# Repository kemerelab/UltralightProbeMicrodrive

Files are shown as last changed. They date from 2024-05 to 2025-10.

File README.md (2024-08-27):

# UltralightProbeMicrodrive
Ultra-light microdrive design for implanted multichannel neural recording probes. 
Remixed from the [microdrive](https://github.com/buzsakilab/3d_print_designs/tree/master/Microdrives/Metal_recoverable) 
designed by Mihály Vöröslakos in the Buzsaki Lab, using a shoulder-screw inspired by the Open Ephys 
[shuttledrive](https://github.com/open-ephys/shuttle-drive) and
[Jadhav Lab](https://gitlab.com/JMOlson/TetDrive-Jadhav-Metal) designs. **Total weight is ~0.7g.**

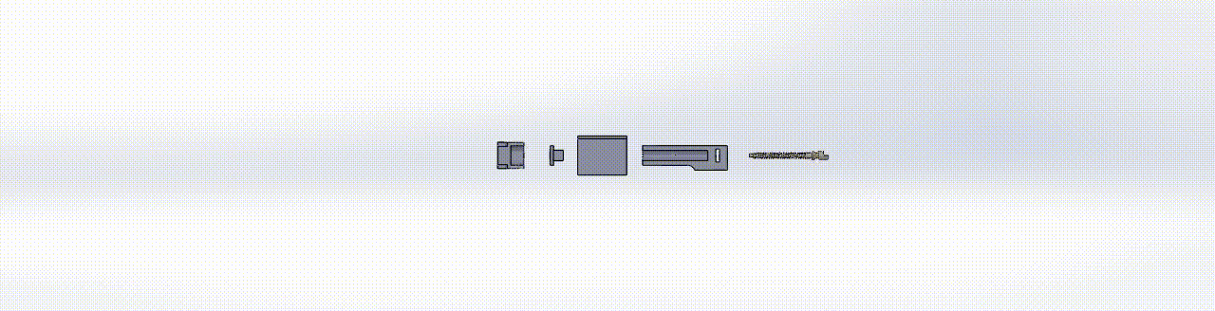
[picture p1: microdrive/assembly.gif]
Microdrive Assembly


Microdrive design is in the `microdrive/` directory. We have printed the microdrive
components using our Projet MJP2500 printer. A number of options exist for MJP2500 prints.
We have had good success with parts recevied from [CadBlu NYC](https://www.cadblu.com/). They
are a distributor for these printers but also print-as-a-service. 
For the shuttle part, we have had good success with lost-wax cast metals. Originally
[Shapeways](https://www.shapeways.com/fragments/product?spin=3TFFV6T2Q) was an easy source,
but since their bankruptcy, we have had success with parts cast from Bronze purchased
via the [CraftCloud3d](https://craftcloud3d.com) marketplace. Bronze is listed in their
"Precious Metals" category. The "Raw" finish was more than adequate. We ordered from a supplier
called "3D Print India" and were quite pleased with both the price and the result. 

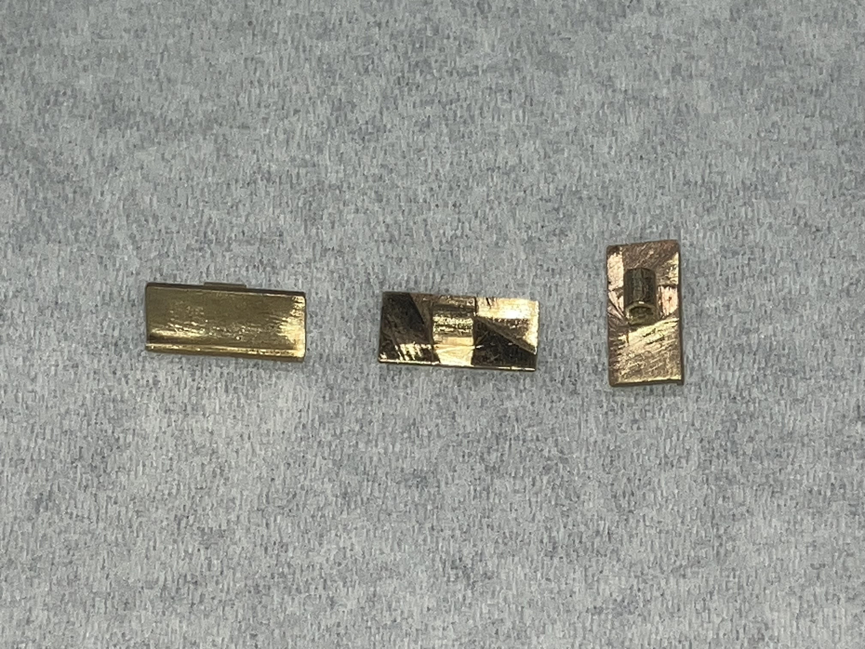
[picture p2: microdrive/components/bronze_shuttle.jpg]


If you want to print the shuttle in plastic rather than metal, we suggest using the 
["for plastic" STL file](https://github.com/ckemere/UltralightProbeMicrodrive/blob/main/microdrive/components/shuttle-split-for-plastic-print.STL).

We have had the custom screws bid on [MFG.com](https://MFG.com), and manufactured 
by [https://g-machining.com/](https://g-machining.com/).
_Contact us with questions, we can provide a small number of screws for testing at cost._

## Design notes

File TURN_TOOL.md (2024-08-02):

# Constructing an Adjustment Tool

Compared to a standard flat head or Phillips (cross drive), the half-cylinder head of the screws
has the advantage of allowing for repeated turning without significant wear. But since it's non standard,
you'll need to construct your own driver tool. 

## Simple Recipe

A simple recipe uses hypodermic tubing in the 16 and 18 gauge sizes (regular wall, available, for example,
at [Component Supply](https://componentsupplycompany.com/product-pages/hypodermictubing.php), and one of
the half-cylinder screws which will be sacrificed to make the mating head inside the tool.

1. The 16 ga tubing will serve as the handle of the tool (unless you use a pin vise or other, fancier,
handle). So cut it long enough to hold comfortably (> 6 cm). 16 ga regular wall tubing has an internal
diameter that just barely admits the entire head of the screw.

2. The 18 ga tubing stabilizes the screw that is used to construct the drive head of the tool. 18 ga tubing
fits precisely inside the 16 ga rw tubing. Its inner diameter tightly contains the threaded part of the
sacrficial tool. This ensures alignment. Thus, the 18 ga tubing needs only to be long enough to contain
the threads of the screw, ~ 1 cm.

3. Cut a couple of slots into the 18 ga tubing, and at least one near the top of the 16 ga tubing. We will
use cyanoacrylate glue to fix everything together, and the slots serve to ensure good binding between
the otherwise very smooth hypodermic surfaces.

4. Put a drop of glue into the 18 ga tube, and insert the screw completely (the threaded part will go in
but not the head). Clean excess glue off the outside and let the glue dry.

5. Once the glue has dried, glue the 18 ga tube / screw assembly into the 16 ga tube. Put a small drop
of glue into the top of the 16 ga tube (the end with the slot in it). Insert the 18 ga tube/screw assembly
and push it in until almost flush - you want the head of the mating screw to be mostly encased by the 16 ga
but not inserted so far that it's top is below the end of the 16 ga (because then it wouldn't mate completely).
If you push it too far by accident, you can stick another tube through the back end of the 16 ga tube to push
it back out before the glue dries.

6. Once the glue has dried completely, you can put a piece of heatshrink on the end of your adjustment tool
to make it easier to hold on to or insert it into a pin vice for a nicer handle!

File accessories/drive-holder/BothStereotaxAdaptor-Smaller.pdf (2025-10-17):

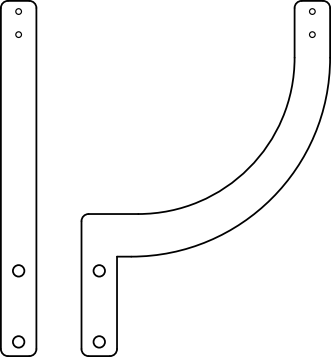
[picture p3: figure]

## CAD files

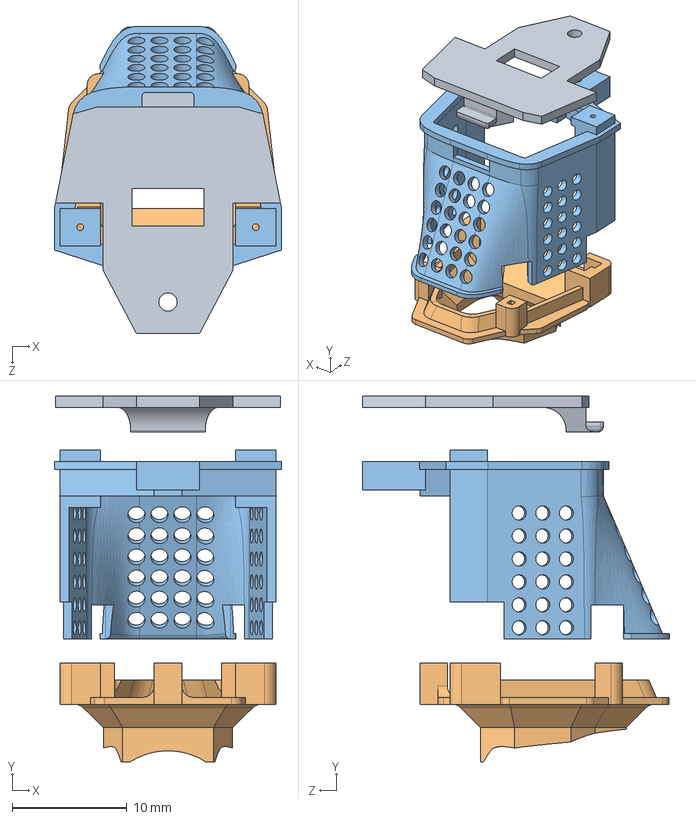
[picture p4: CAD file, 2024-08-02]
accessories/mouse-cover/mouse-cover-lighter.SLDASM
19.8 x 31.9 x 26.8 mm
cover-cap-split
mouse-base-split
protective-cover-split

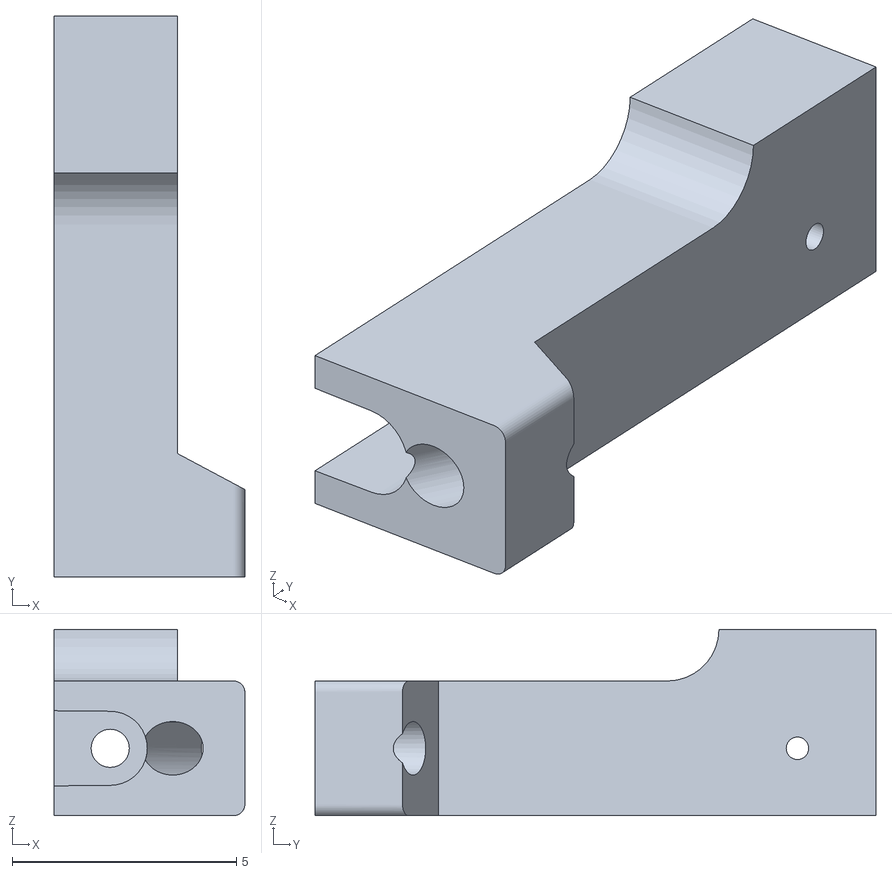
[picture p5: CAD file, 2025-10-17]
microdrive/components/main-drive-channel-split-convex.STL
4.25 x 12.5 x 4.15

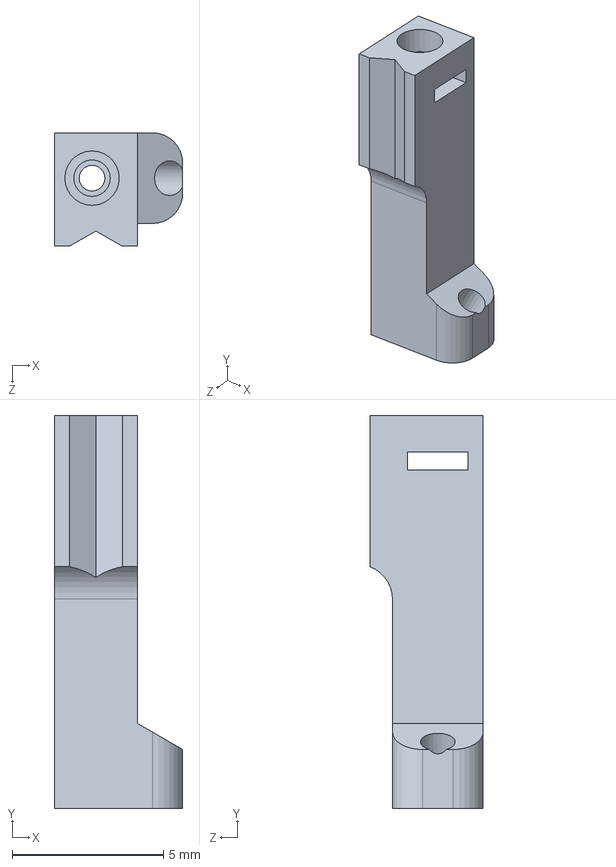
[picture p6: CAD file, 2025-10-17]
microdrive/components/main-drive-channel-agressive.SLDPRT
4.25 x 13.0 x 3.75 mm

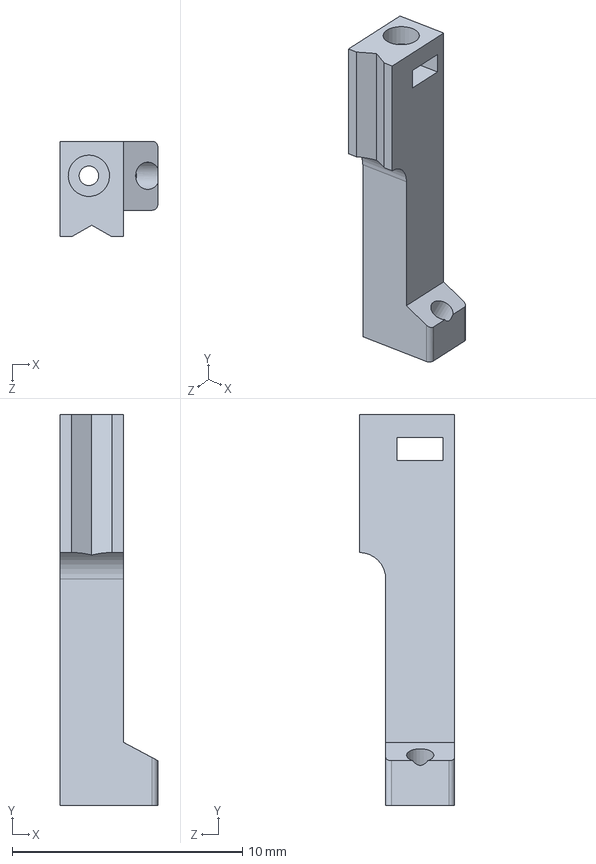
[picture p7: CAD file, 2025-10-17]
microdrive/components/main-drive-channel-rat-insert-split.SLDPRT
4.25 x 17.0 x 4.15 mm

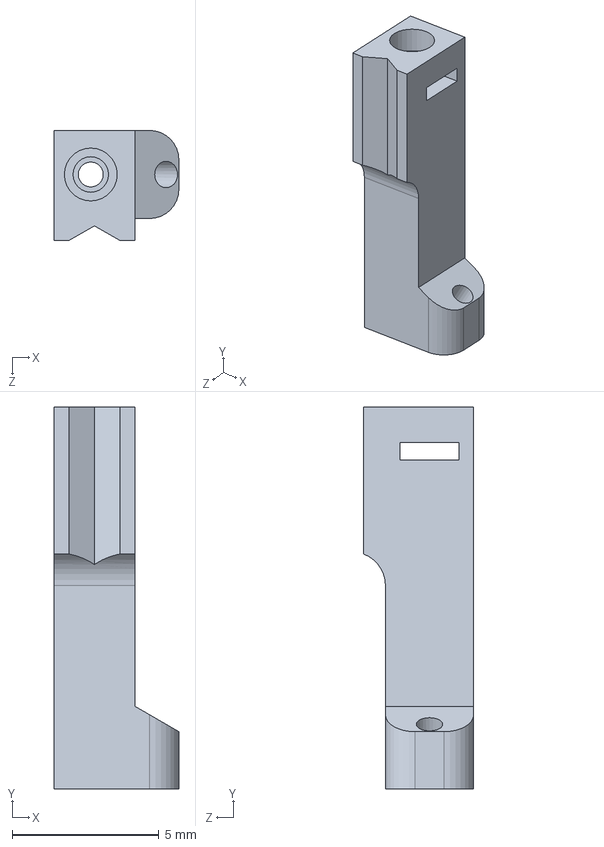
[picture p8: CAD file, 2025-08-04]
microdrive/components/main-drive-channel.SLDPRT
4.25 x 13.0 x 3.75 mm

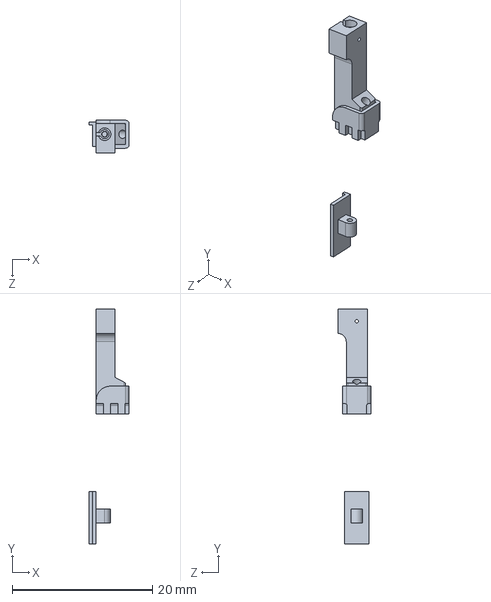
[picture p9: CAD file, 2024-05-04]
microdrive/components/Assem1.SLDASM
5.75 x 33.5 x 4.65 mm

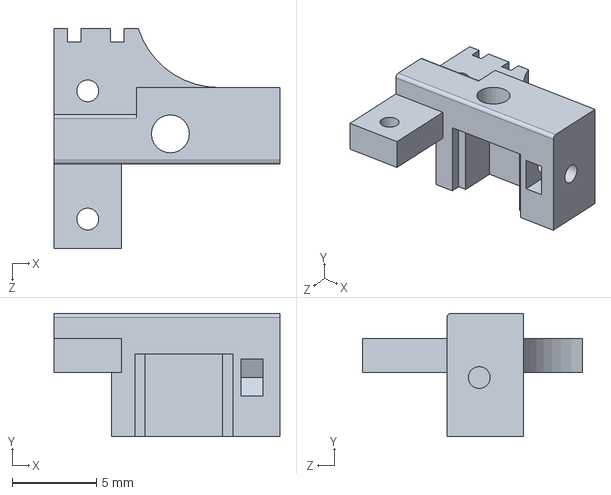
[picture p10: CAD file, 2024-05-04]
accessories/drive-holder-for-stereotax-adaptor.sldprt
13.4 x 7.30 x 13.1 mm

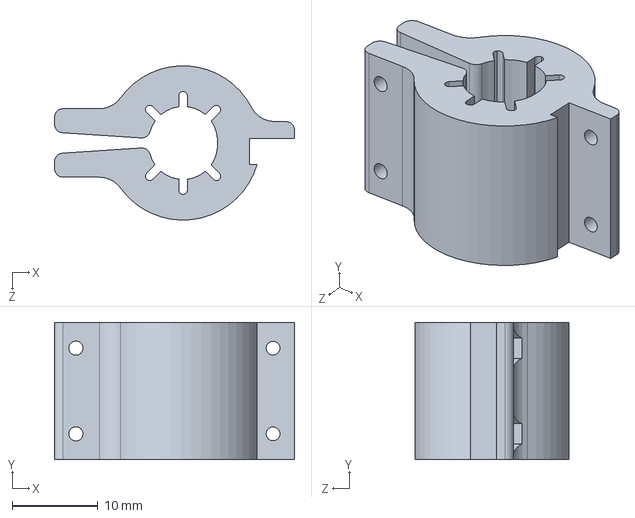
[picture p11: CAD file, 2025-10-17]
accessories/drive-holder/StereotaxAdaptorForBrassHolder.SLDPRT
28.0 x 16.0 x 18.0 mm

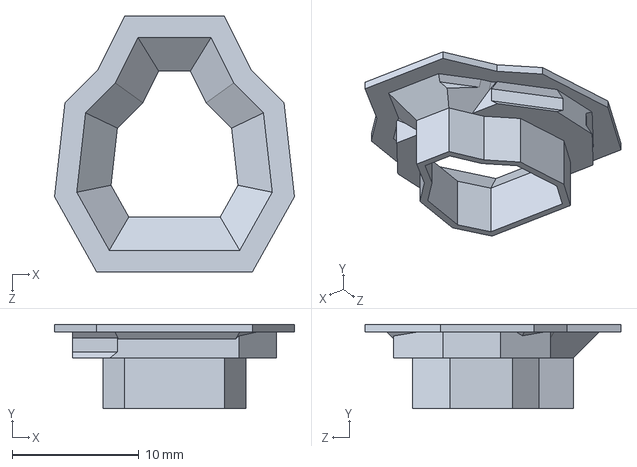
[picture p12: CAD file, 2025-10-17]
accessories/mouse-cover-headfixation/lightweight-cover-head-fixation.SLDPRT
18.9 x 6.63 x 20.2 mm

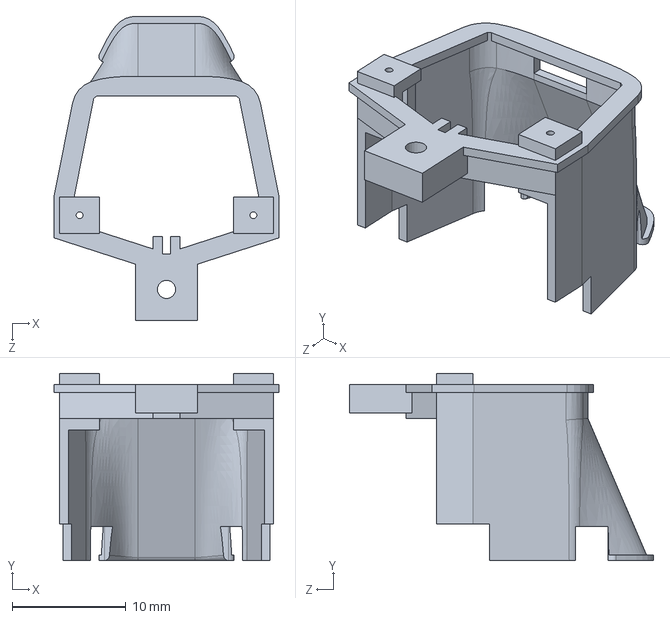
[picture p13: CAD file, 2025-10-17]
accessories/mouse-cover/components/protective-cover-noholes-split.SLDPRT
19.8 x 16.5 x 26.8 mm

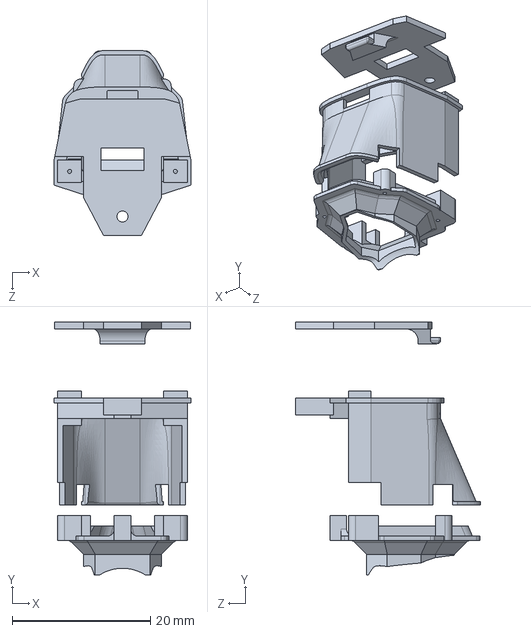
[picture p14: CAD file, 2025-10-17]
accessories/mouse-cover/lightweight-cover-noholes.SLDPRT
19.8 x 36.6 x 26.8 mm

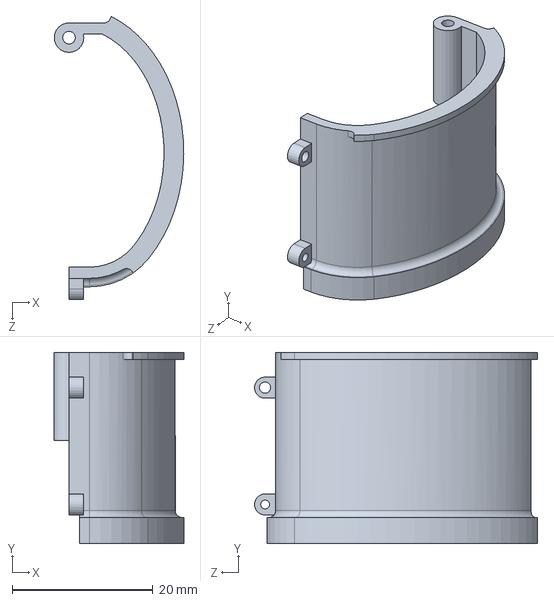
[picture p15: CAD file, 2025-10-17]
accessories/rat-cover/components/right-wall-four-slots-derived-no-slots.SLDPRT
18.4 x 27.2 x 40.2 mm

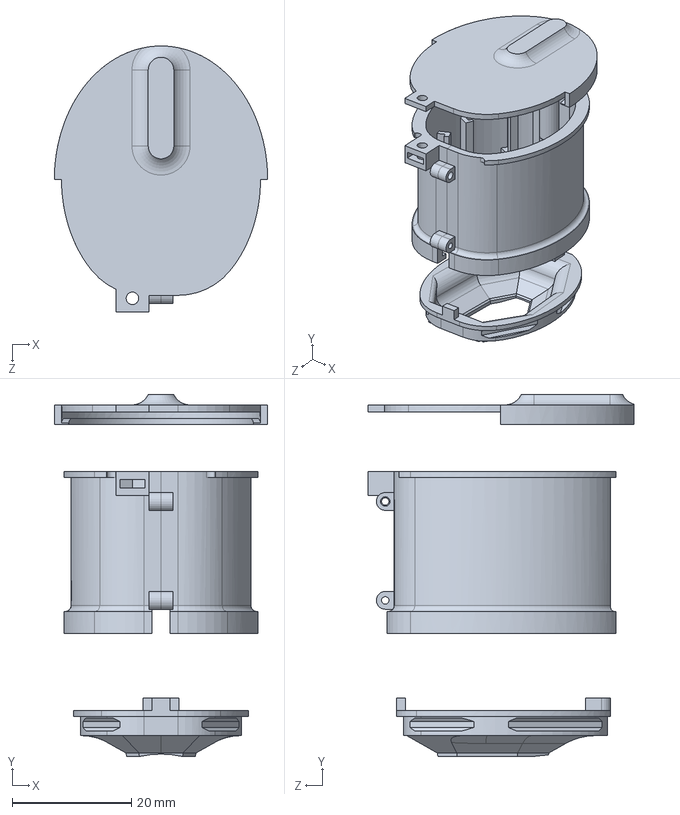
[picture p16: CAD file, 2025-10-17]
accessories/rat-cover/rat-cap-headfixed-four-slots.SLDPRT
35.8 x 60.8 x 44.6 mm

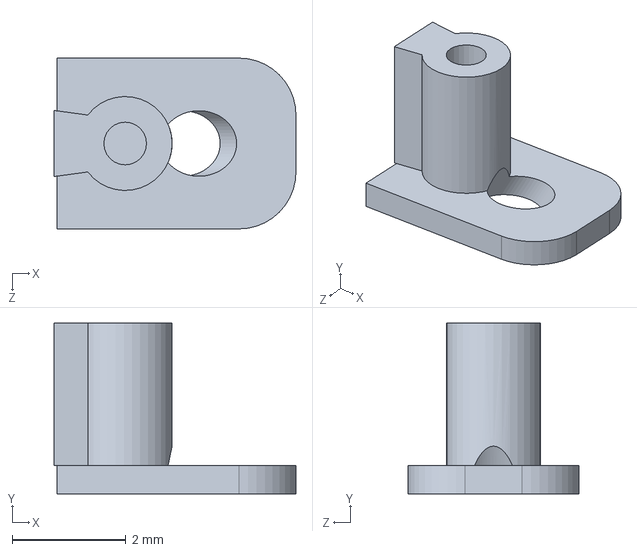
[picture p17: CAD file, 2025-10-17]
microdrive/components/base-insert-agressive-unchanged-longer.SLDPRT
4.25 x 3.00 x 3.00 mm

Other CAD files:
microdrive/microdrive-assembly.SLDASM
accessories/mouse-cover/mouse-cover.SLDASM
microdrive/components/main-drive-channel-split.SLDPRT
accessories/mouse-cover-headfixation/components/cover-cap-head-fixed-split.SLDPRT
accessories/drive-holder-for-stereotax-adaptor.stl
accessories/drive-holder/Holder.SLDPRT
accessories/drive-holder/Holder.STL
accessories/drive-holder/StereotaxAdaptorForBrassHolder.STL
accessories/mouse-cover-headfixation/components/cover-cap-head-fixed-split.STL
accessories/mouse-cover-headfixation/components/mouse-base-head-fixed-split.SLDPRT
accessories/mouse-cover-headfixation/components/mouse-base-head-fixed-split.STL
accessories/mouse-cover-headfixation/components/protective-cover-head-fixed-split.SLDPRT
accessories/mouse-cover-headfixation/components/protective-cover-head-fixed-split.STL
accessories/mouse-cover/components/cover-cap-noholes-split.SLDPRT
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

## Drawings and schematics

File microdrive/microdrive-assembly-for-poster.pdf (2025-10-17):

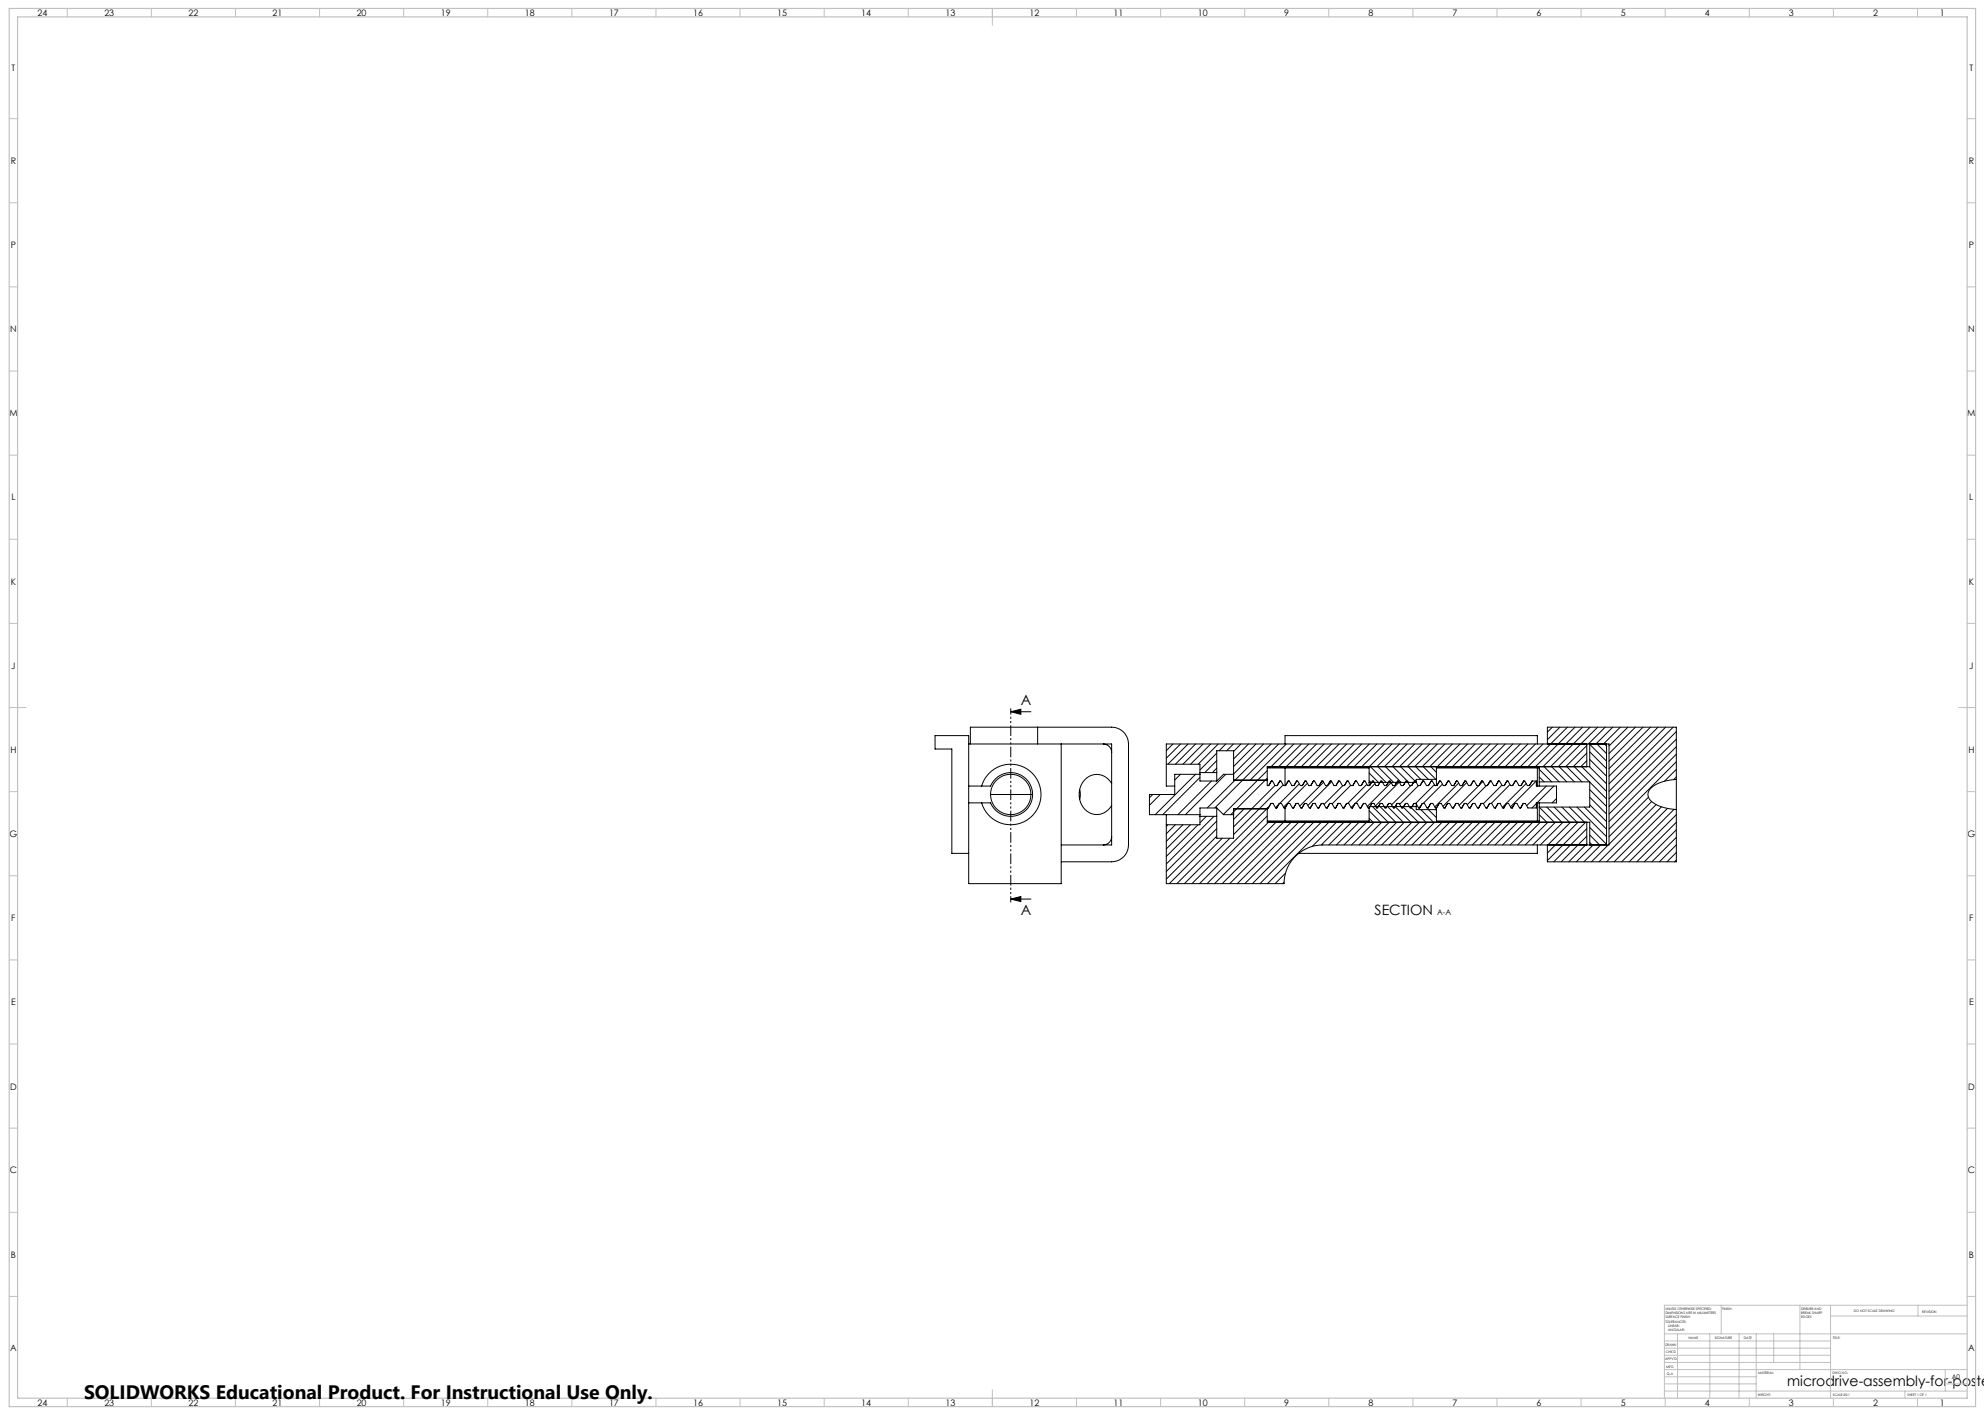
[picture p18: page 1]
SECTION A-A; FINISH:; DEBURR AND; BREAK SHARP; DO NOT SCALE DRAWING; REVISION; SCALE:20:1; SHEET 1 OF 1

UNLESS OTHERWISE SPECIFIED:
DIMENSIONS ARE IN MILLIMETERS
SURFACE FINISH:
TOLERANCES:
LINEAR:
ANGULAR:

NAME | SIGNATURE | DATE | | | | TITLE:

microdrive-assembly-for-poster SOLIDWORKS Educational Product. For Instructional Use Only.

DRAWN
CHK'D
APPV'D
MFG
Q.A | | | | MATERIAL: | DWG NO. | A0

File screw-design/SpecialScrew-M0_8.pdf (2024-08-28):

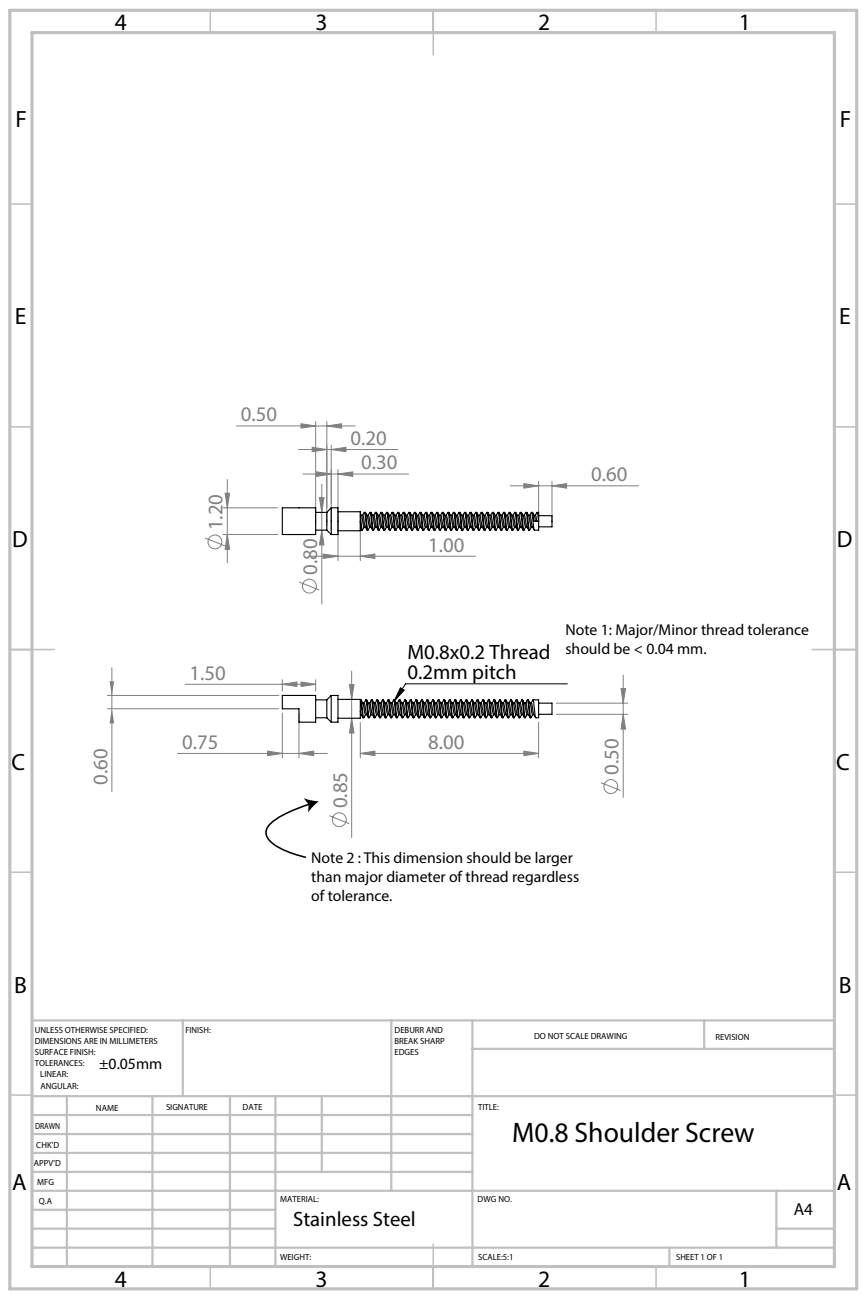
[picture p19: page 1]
M0.8x0.2 Thread 0.2mm pitch; FINISH:; DEBURR AND; BREAK SHARP; DO NOT SCALE DRAWING; REVISION; SCALE:5:1; SHEET 1 OF 1

Note 1: Major/Minor thread tolerance
should be < 0.04 mm.

Note 2 : This dimension should be larger
than major diameter of thread regardless
of tolerance.

UNLESS OTHERWISE SPECIFIED:
DIMENSIONS ARE IN MILLIMETERS
SURFACE FINISH:
TOLERANCES:
LINEAR:
ANGULAR:

NAME | SIGNATURE | DATE | | | | TITLE: M0.8 Shoulder Screw

DRAWN
CHK'D
APPV'D
MFG
Q.A | | | | MATERIAL: Stainless Steel | DWG NO. | A4

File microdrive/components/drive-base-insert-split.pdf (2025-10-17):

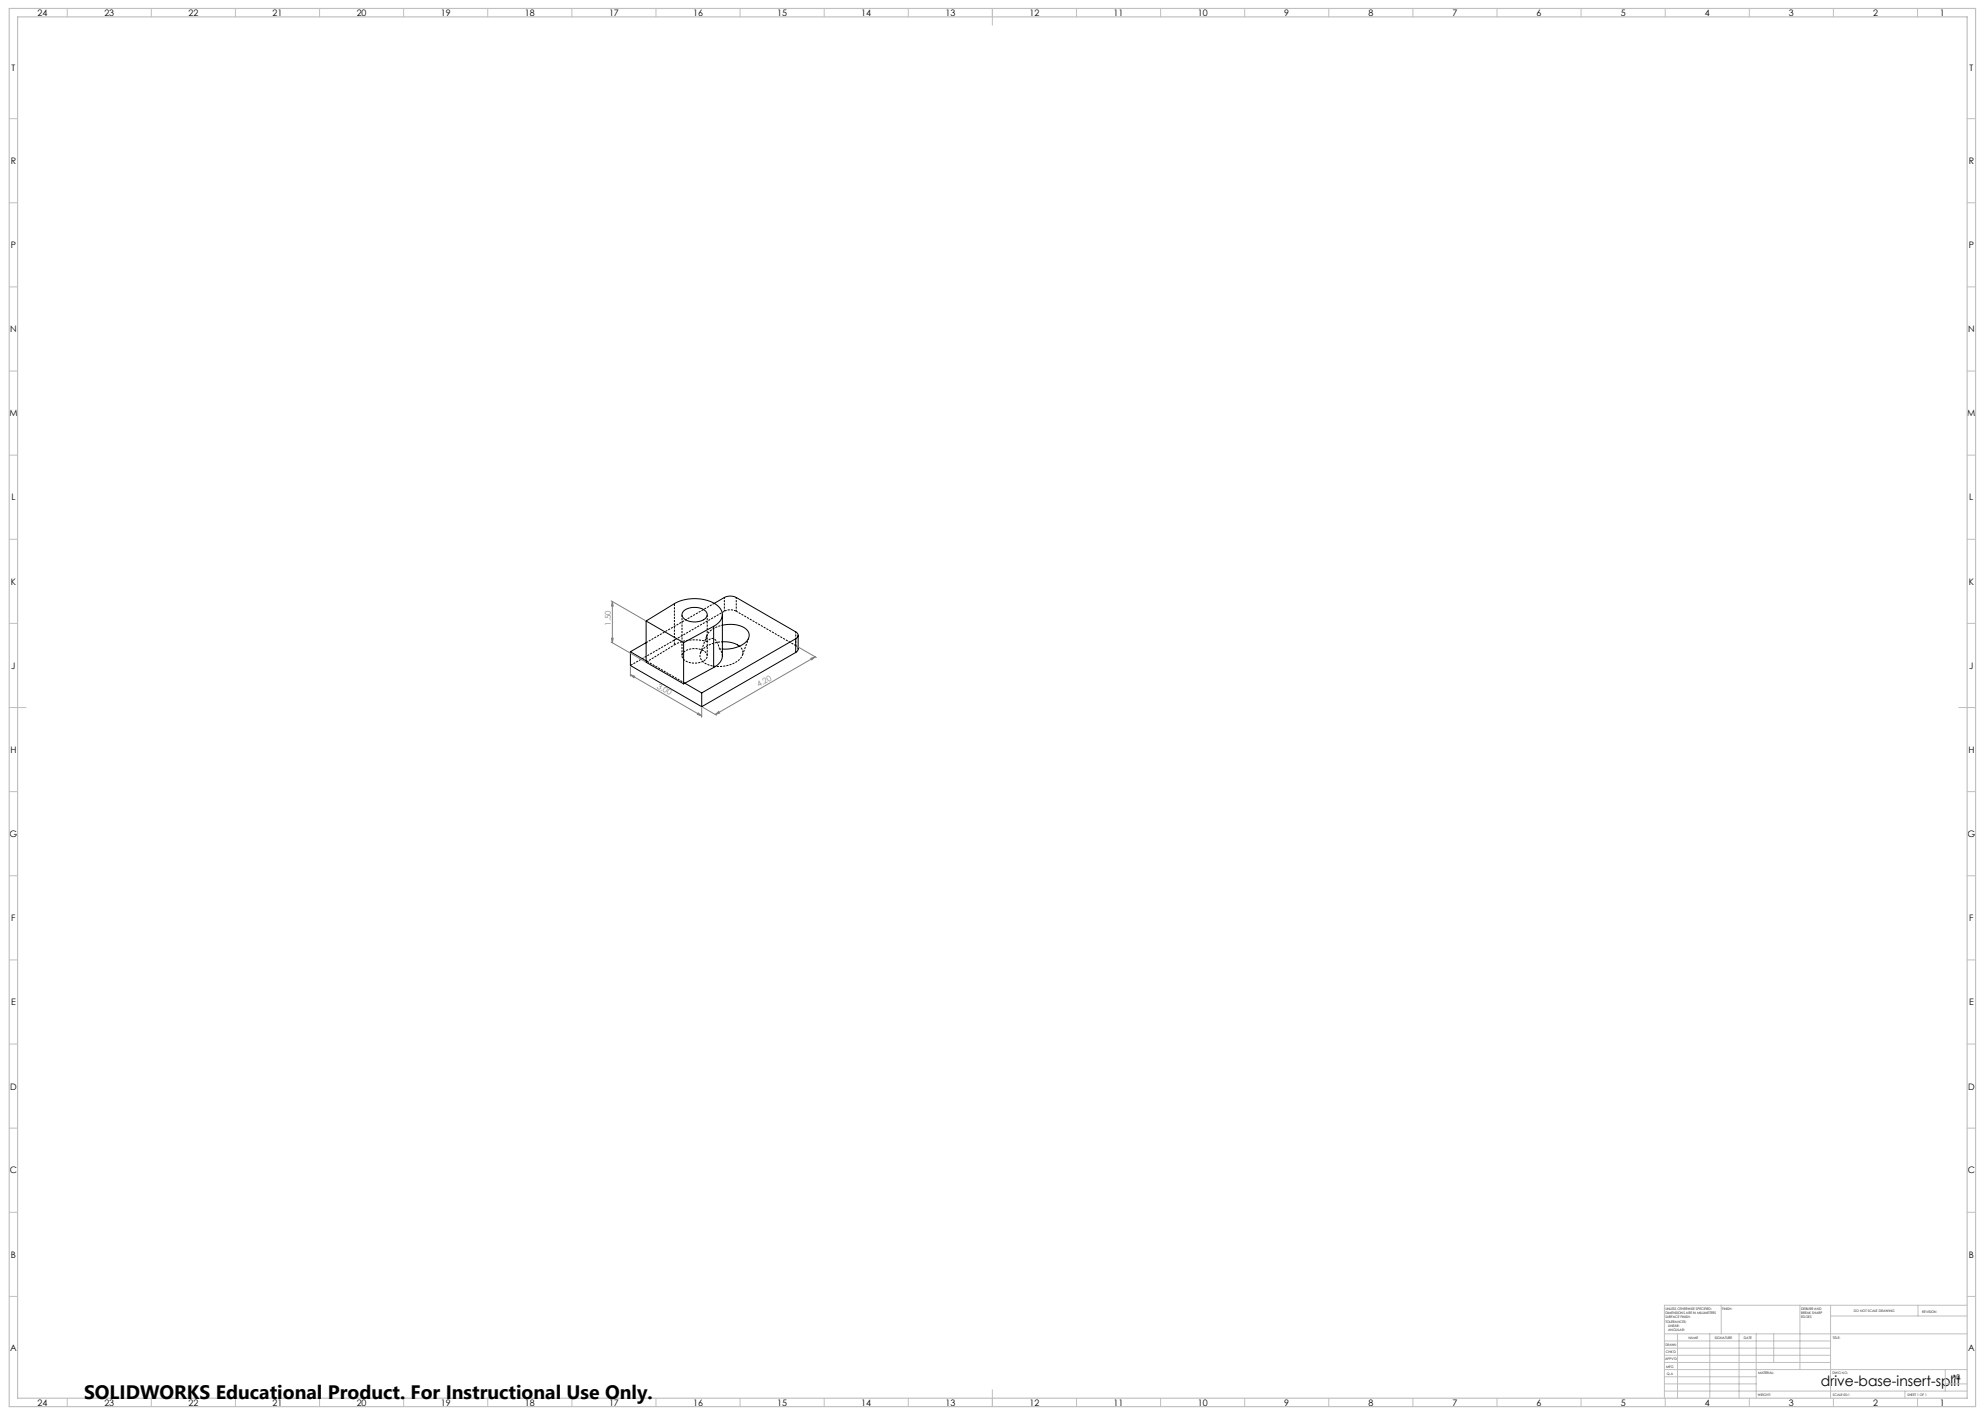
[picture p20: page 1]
FINISH:; DEBURR AND; BREAK SHARP; DO NOT SCALE DRAWING; REVISION; SCALE:50:1; SHEET 1 OF 1

UNLESS OTHERWISE SPECIFIED:
DIMENSIONS ARE IN MILLIMETERS
SURFACE FINISH:
TOLERANCES:
LINEAR:
ANGULAR:

NAME | SIGNATURE | DATE | | | | TITLE:

drive-base-insert-split SOLIDWORKS Educational Product. For Instructional Use Only.

DRAWN
CHK'D
APPV'D
MFG
Q.A | | | | MATERIAL: | DWG NO. | A0

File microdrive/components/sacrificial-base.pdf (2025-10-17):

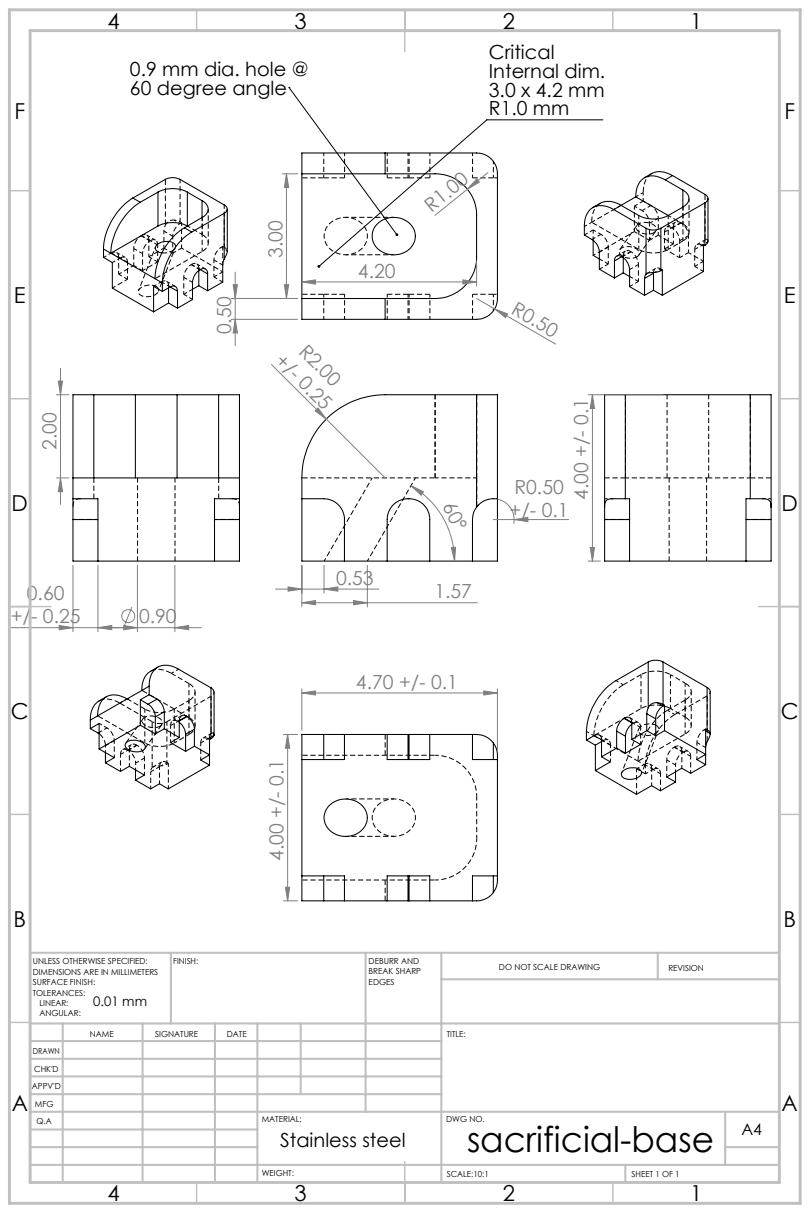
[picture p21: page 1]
60 degree angle; Internal dim. 3.0 x 4.2 mm R1.0 mm; FINISH:; DEBURR AND; BREAK SHARP; DO NOT SCALE DRAWING; REVISION; SCALE:10:1; SHEET 1 OF 1

0.9 mm dia. hole @

UNLESS OTHERWISE SPECIFIED:
DIMENSIONS ARE IN MILLIMETERS
SURFACE FINISH:
TOLERANCES:
LINEAR:
ANGULAR:

NAME | SIGNATURE | DATE | | | | TITLE:

DRAWN
CHK'D
APPV'D
MFG
Q.A | | | | MATERIAL: Stainless steel | DWG NO. sacrificial-base | A4

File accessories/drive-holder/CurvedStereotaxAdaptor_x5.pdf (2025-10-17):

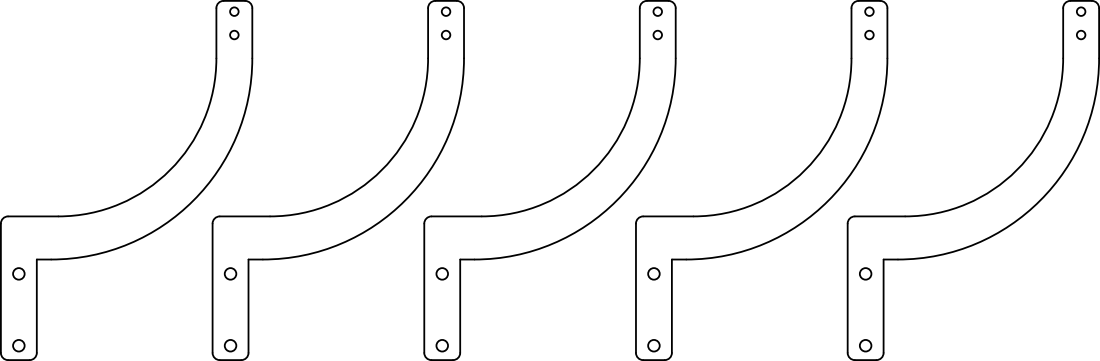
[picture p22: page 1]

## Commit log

2024-05-04 Added animated gif of assembly
    [Assem1.SLDASM, SpecialScrew-M0_8.SLDDRW, SpecialScrew-M0_8.SLDPRT, baseplate-split.SLDPRT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]
2024-05-04 Added STL for plastic shuttle
    [shuttle-split-for-plastic-print.STL]
2024-05-04 Removed wrongly named file
    [shuttle-split-for-3d-print.SLDPRT]
2024-08-02 Added lighter cover (which actually is probably not necessary).
    [cover-cap-split.SLDPRT, cover-cap-split.STL, drive-base-insert-split.SLDPRT, lightweight-cover.sldprt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]
2024-08-27 Updated insertion of shuttle picture to resize.
2024-08-27 Updated insertion of shuttle picture to resize and go below text.
2024-08-28 Added a dimension to screw design doc
2024-08-30 Added a dimension to screw drawing and other 3D file formats
    [SpecialScrew-M0_8.IGS, SpecialScrew-M0_8.STEP, SpecialScrew-M0_8.STL]
2024-10-14 Upated shuttle to make hole full size all the way.
    [shuttle-split.SLDPRT, shuttle-split.STL]
2024-10-14 Added a neuropixel shuttle.
    [shuttle-split-wide.STL]
2025-08-04 Added head fixed mouse cover
    [cover-cap-head-fixed-split.SLDPRT, cover-cap-head-fixed-split.STL, lightweight-cover-head-fixation.SLDPRT, mouse-base-head-fixed-split.SLDPRT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]
2025-08-04 Version 2.0 updates. Grooved channel for fixation, new holder, interior curve in sacrificial base.
    [90910A632_Button Head Torx Screws.SLDPRT, Holder.SLDPRT, Holder.STL, SpecialScrew-M0_8.SLDPRT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]
2025-10-17 Updated for brass. Working well
    [baseplate-split.SLDPRT, baseplate-split.STL, cap-split.SLDPRT, cap-split.STL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]
2025-10-17 Updated rat cover
    [cap-four-slots.SLDPRT, cap-four-slots.STL, head-fixed-base-four-slots-not-headfixed.SLDPRT, head-fixed-base-four-slots-not-headfixed.STL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]
2025-10-17 Kitchen sink
    [base-insert-agressive-unchanged-longer.SLDPRT, base-insert-agressive-unchanged-longer.STL, base-insert-agressive-unchanged.SLDPRT, base-insert-longer.SLDPRT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]
2025-10-17 Added plastic piece for brass drive holder
    [StereotaxAdaptorForBrassHolder.SLDPRT, StereotaxAdaptorForBrassHolder.STL]
